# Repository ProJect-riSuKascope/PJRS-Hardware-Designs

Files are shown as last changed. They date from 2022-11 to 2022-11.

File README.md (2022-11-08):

# Project RisukaScope硬件系统
硬件系统主要分为以下几个部分：

## 电源
`/Power`文件夹。  
一个基于XL4016/SY8253的6~9V/5V/3.3V三轨供电系统。
此外还有一个给模拟前端用的5V模拟电源输出，用了一个LM1117-5.0。  
这部分十分臃肿，所以之后会做一个新的出来。

## 射频前端
`/RFFE`文件夹。  
前端LNA+滤波+多级Gain Block放大。  
前端LNA是NXP的BGU8009 GNSS LNA。  
滤波器是TA2494A。SAW滤波器，中心频率1420MHz，带宽80MHz。  
Gain Block用的是烂大街的SBB5089。  
Qucs仿真得到这个电路的增益~56dB，NF~0.66dB；实测增益48dB，NF因条件有限未测试。

## 调谐器与ADC
`Tuner ADC`文件夹。调谐器用的是各类SDR设备上常见的MSI001芯片，只用了L Band端口。实际试了一下应该有8MHz的带宽。  
ADC用的是AD9201，I/Q双通道同步采样ADC。  
系统采样率16MSPS。

## 通信与用户界面
`/Connectivity Interface`文件夹。
用了个ESP32-C3实现蓝牙/Wi-Fi通信。ESP32-C3通过SPI连接到FPGA。  
CD4504做缓冲器驱动舵机。  
预留了RGB LCD和以太网模块的接口。但目前还没用上。  
下面预留了八个机械键盘轴和两个电位器的位置，用于机械结构的操控。  
但后来想了想，感觉这样一点也不好用，不如直接遥控了。  
因为很多东西都没啥卵用，所以这部分也要大改。

## PMOD-Flash TinyRTC
`PMOD-Flash`文件夹。  
仿照Arduino平台上曾红极一时的I2C TinyRTC模块设计的PMOD Flash+RTC模块。  
一个W25N01 Flash+RX8010 RTC。RTC备份电源用的是硬币状的超级电容器。

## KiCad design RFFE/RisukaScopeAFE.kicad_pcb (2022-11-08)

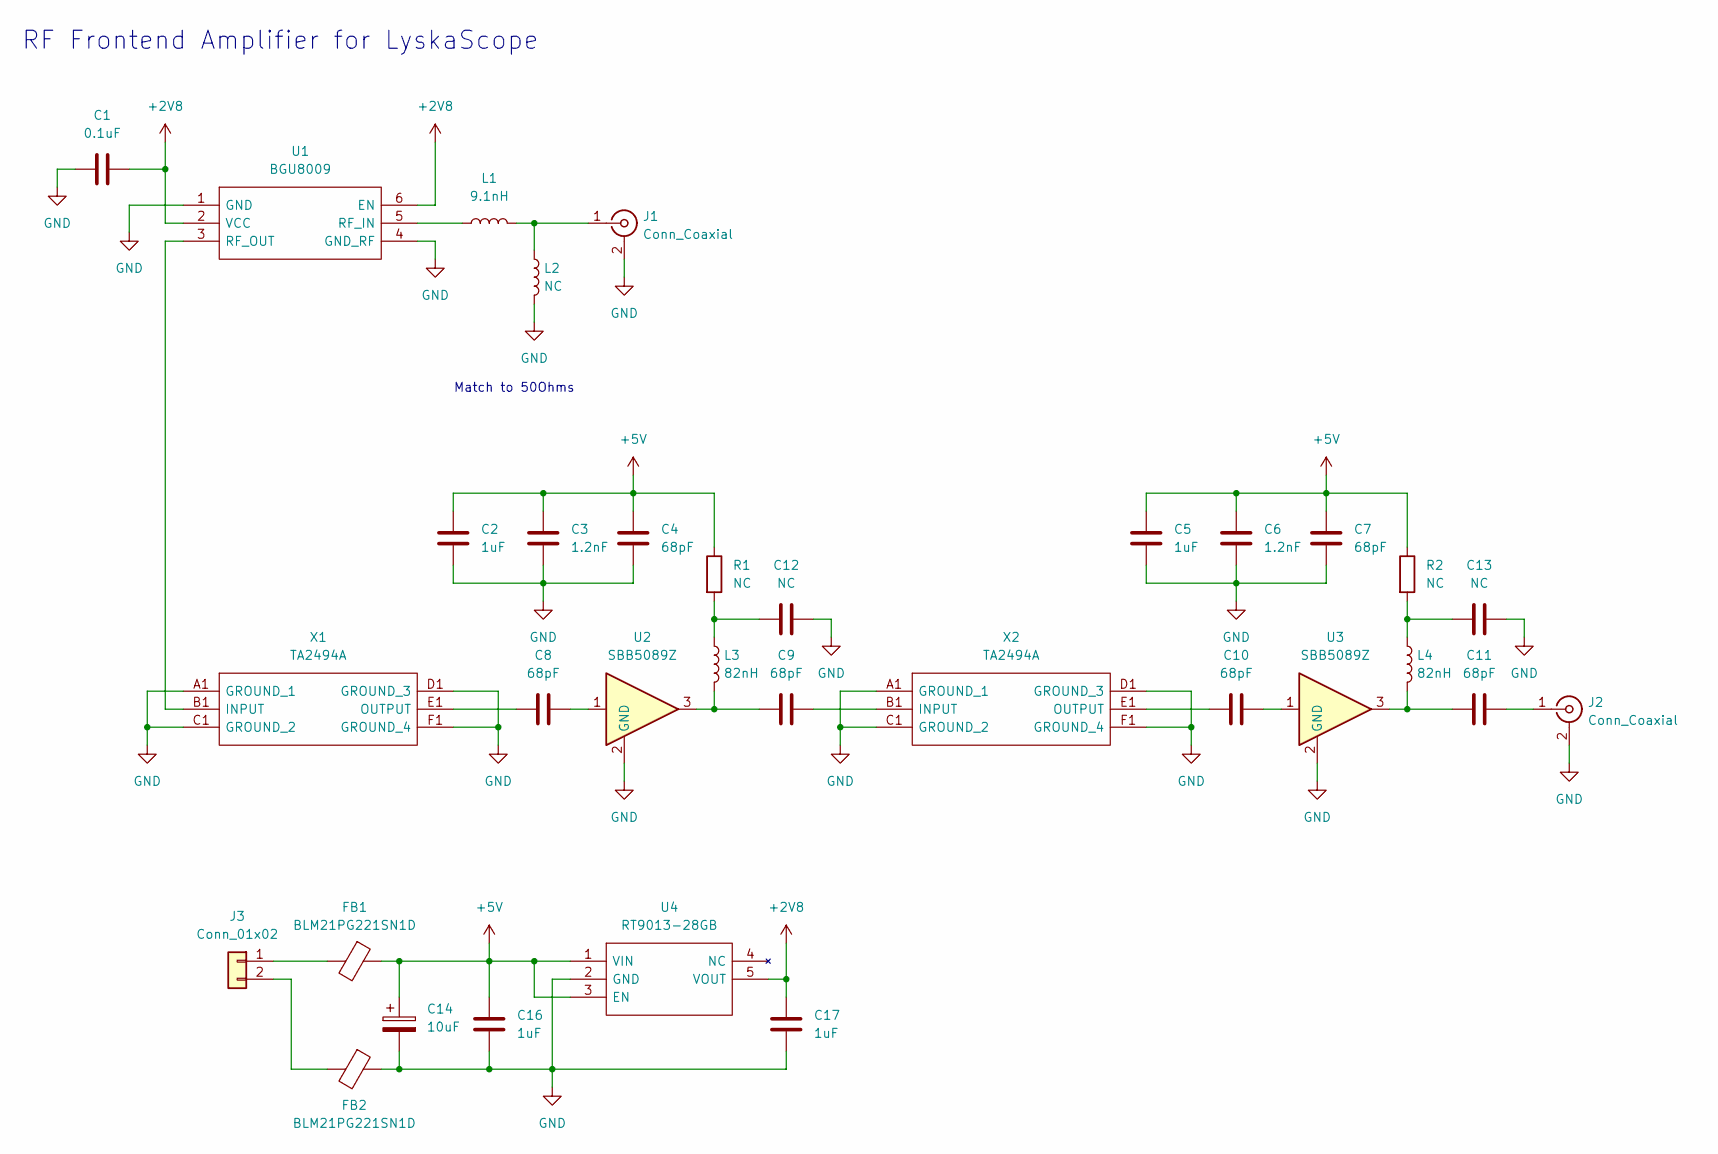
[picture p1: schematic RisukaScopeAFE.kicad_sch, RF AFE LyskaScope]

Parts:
C1: 0.1uF; C_0603_1608Metric
C2, C5, C16, C17: 1uF; C_0603_1608Metric
C3, C6: 1.2nF; C_0603_1608Metric
C4, C7, C8, C9, C10, C11: 68pF; C_0603_1608Metric
C12, C13: NC; C_0603_1608Metric
C14: 10uF; CP_EIA-3216-18_Kemet-A
FB1, FB2: BLM21PG221SN1D; L_0805_2012Metric
J1, J2: Conn_Coaxial; SMA_Samtec_SMA-J-P-X-ST-EM1_EdgeMount
J3: Conn_01x02; PinHeader_1x02_P2.54mm_Vertical
L1: 9.1nH; L_0603_1608Metric
L2: NC; L_0603_1608Metric
L3, L4: 82nH; L_0603_1608Metric
R1, R2: NC; R_0805_2012Metric
U1: BGU8009; SL3S1013FTB0115; Manufacturer_Part_Number BGU7005,115; Mouser Part Number 771-BGU7005115
U2, U3: SBB5089Z; SOT-89-3
U4: RT9013-28GB; SOT94P279X130-5N; Manufacturer_Part_Number RT9013-33GB
X1, X2: TA2494A; Manufacturer_Part_Number TA2494A

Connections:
+2V8: C1.1, C17.1, U1.2 (VCC), U1.6 (EN), U4.5 (VOUT)
+5V: C2.1, C3.1, C4.1, C5.1, C6.1, C7.1, C14.1, C16.1, FB1.1, R1.1, R2.1, U4.1 (VIN), U4.3 (EN)
GND: C1.2, C2.2, C3.2, C4.2, C5.2, C6.2, C7.2, C12.2, C13.2, C14.2, C16.2, C17.2, FB2.1, J1.2 (Ext), J2.2 (Ext), L2.2, U1.1 (GND), U1.4 (GND_RF), U2.2 (GND), U3.2 (GND), U4.2 (GND), X1.A1 (GROUND_1), X1.C1 (GROUND_2), X1.D1 (GROUND_3), X1.F1 (GROUND_4), X2.A1 (GROUND_1), X2.C1 (GROUND_2), X2.D1 (GROUND_3), X2.F1 (GROUND_4)
unnamed: C8.1, U2.1
unnamed: C8.2, X1.E1 (OUTPUT)
unnamed: C9.1, X2.B1 (INPUT)
unnamed: C9.2, L3.2, U2.3
unnamed: C10.1, U3.1
unnamed: C10.2, X2.E1 (OUTPUT)
unnamed: C11.1, J2.1 (In)
unnamed: C11.2, L4.2, U3.3
unnamed: FB1.2, J3.1
unnamed: FB2.2, J3.2
unnamed: J1.1 (In), L1.2, L2.1
unnamed: L1.1, U1.5 (RF_IN)
unnamed: C12.1, L3.1, R1.2
unnamed: C13.1, L4.1, R2.2
unnamed: U1.3 (RF_OUT), X1.B1 (INPUT)

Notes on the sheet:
Match to 50Ohms
RF Frontend Amplifier for LyskaScope

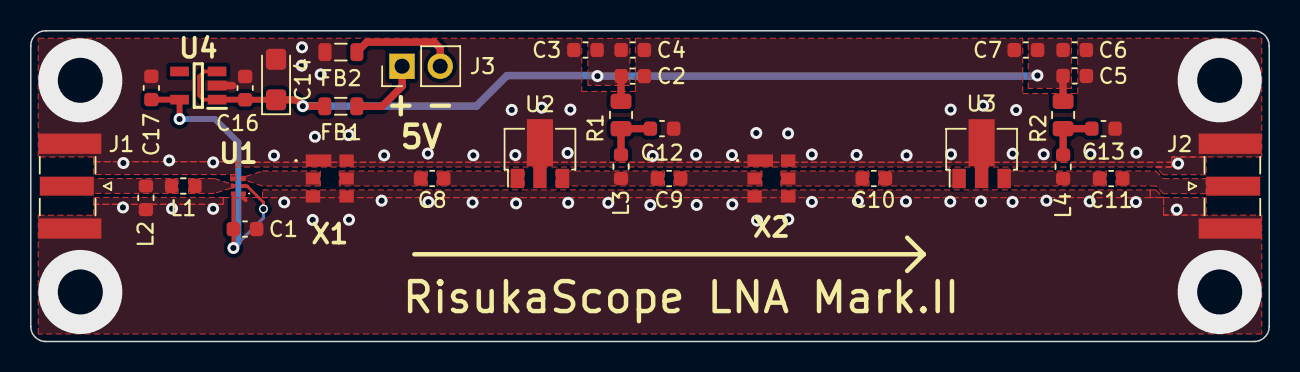
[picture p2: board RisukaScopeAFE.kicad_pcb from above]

Board: 2 copper layers, 82.5 x 20.7 mm, 33 parts (0 on the bottom side), 18 nets.

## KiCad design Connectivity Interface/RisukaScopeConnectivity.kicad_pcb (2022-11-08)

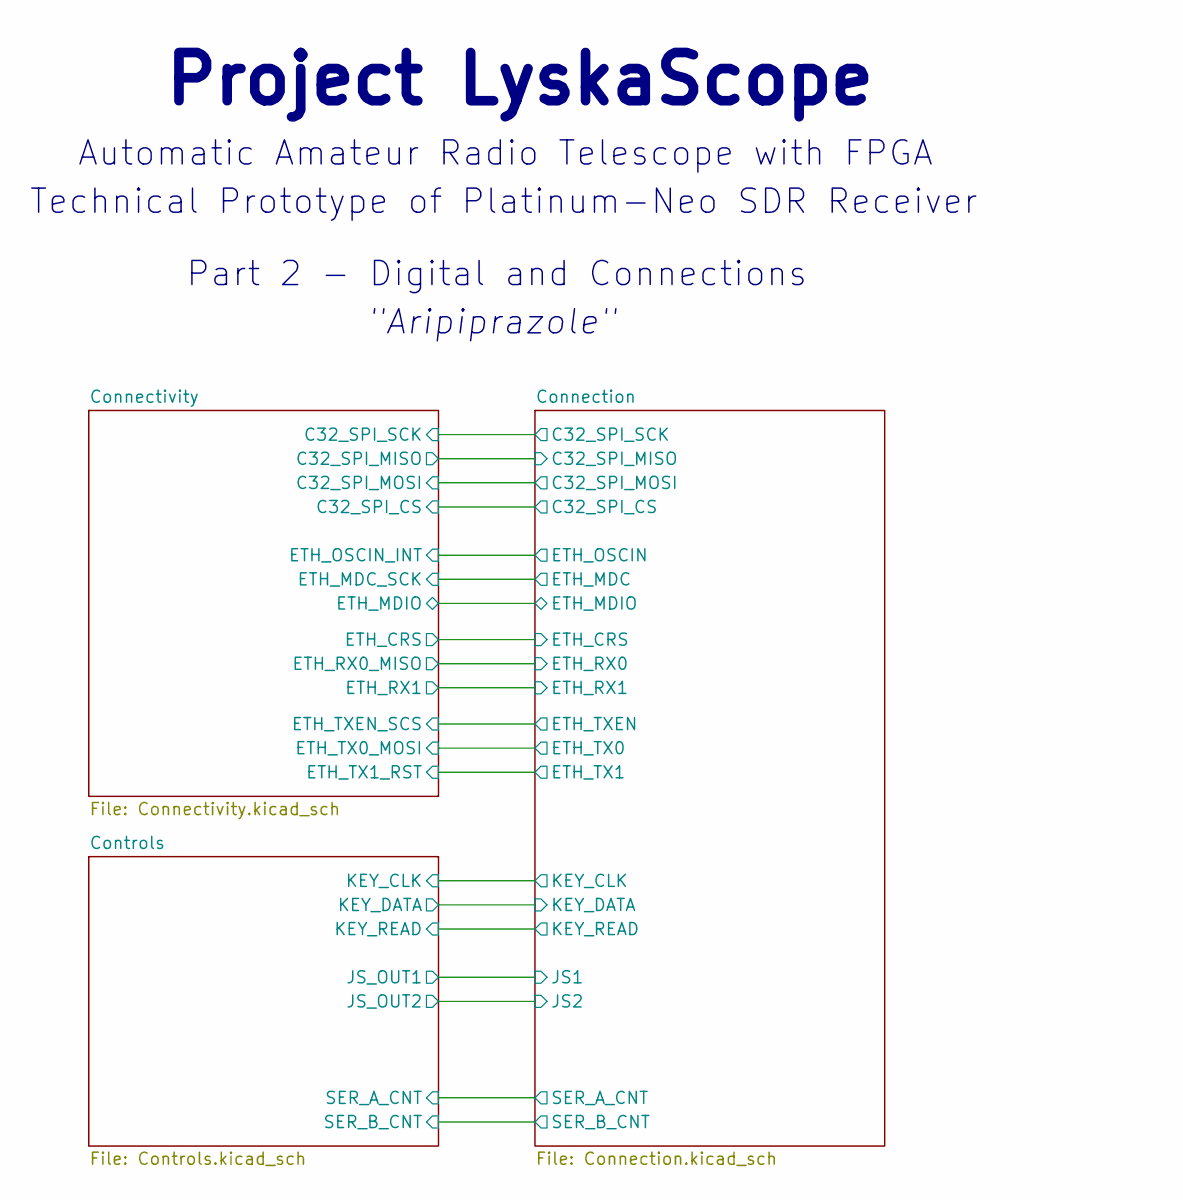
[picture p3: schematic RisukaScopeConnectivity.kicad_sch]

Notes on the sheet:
Project LyskaScope
Technical Prototype of Platinum-Neo SDR Receiver
"Aripiprazole"
Part 2 - Digital and Connections
Automatic Amateur Radio Telescope with FPGA

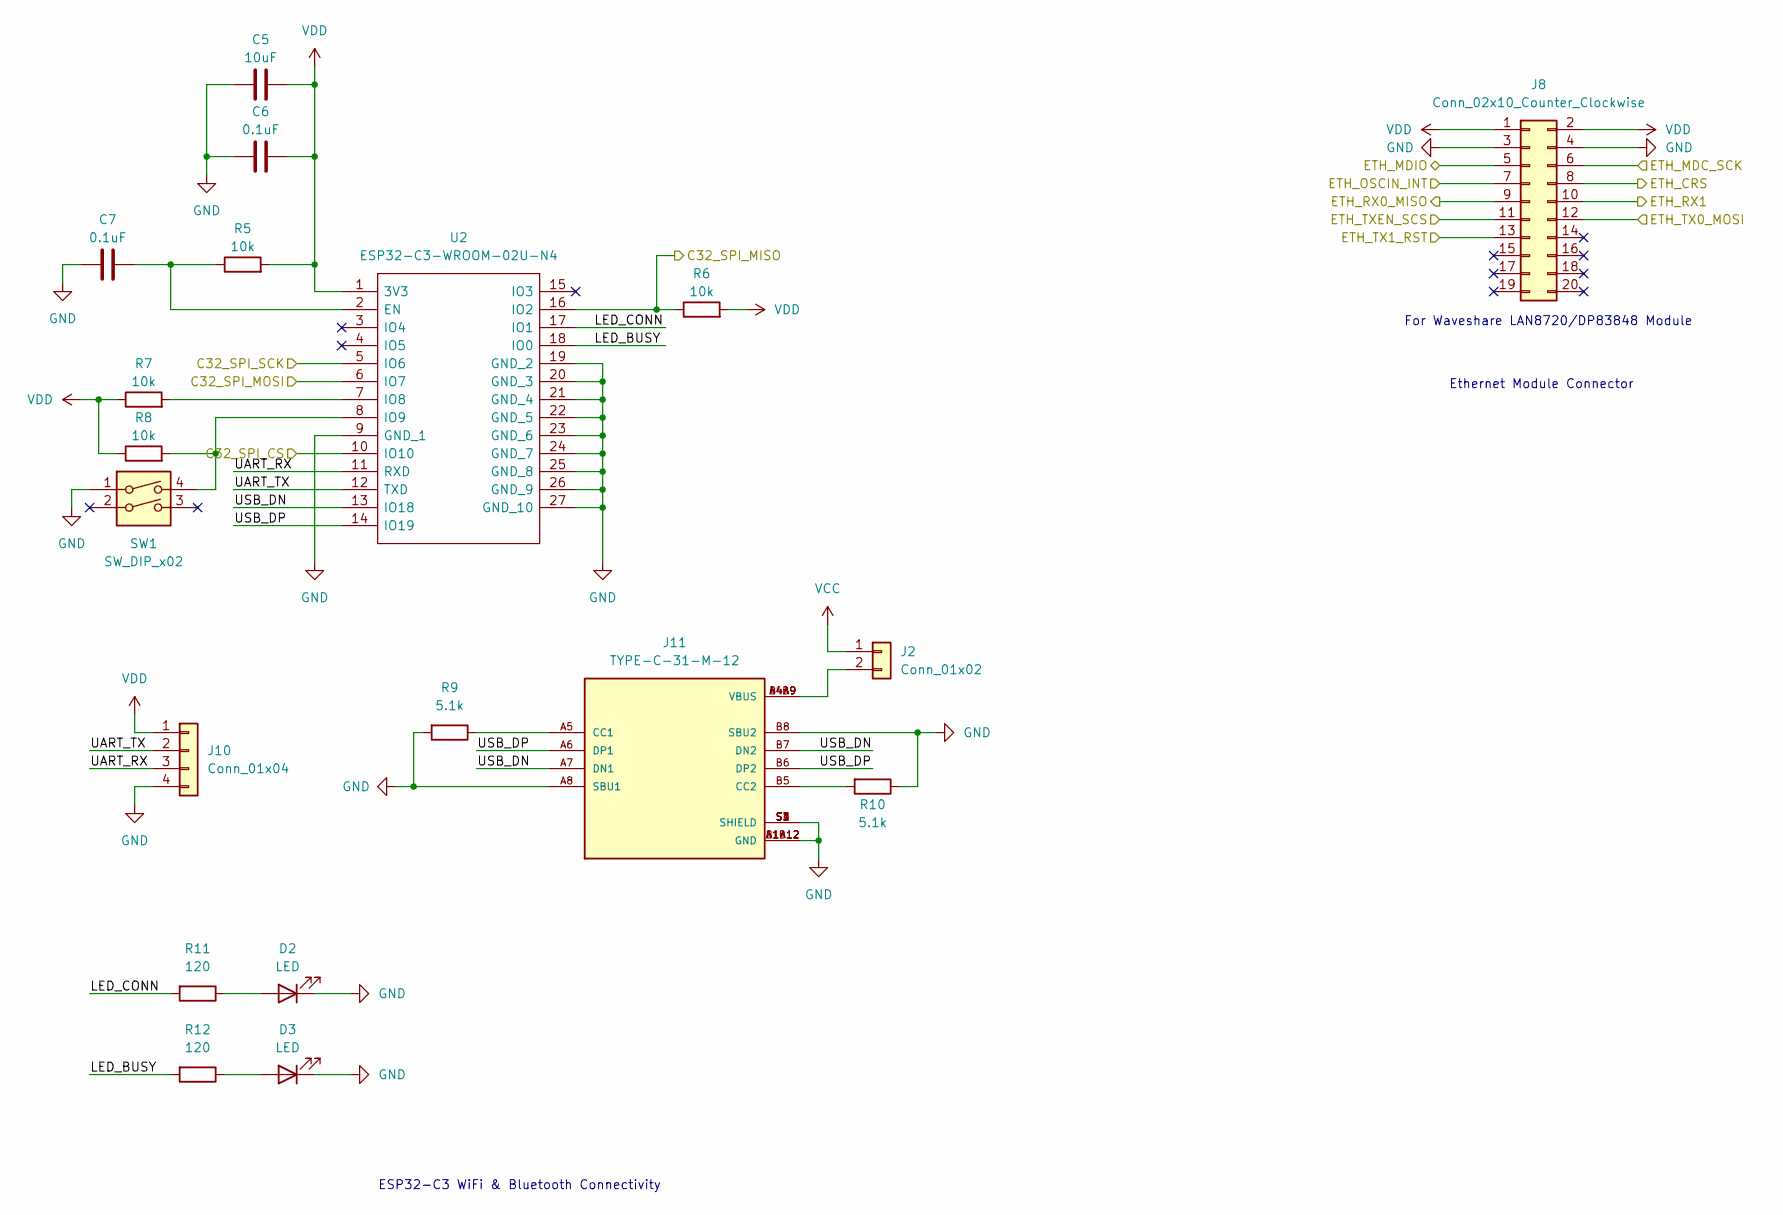
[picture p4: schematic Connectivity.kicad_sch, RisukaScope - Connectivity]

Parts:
C5: 10uF; C_0603_1608Metric
C6, C7: 0.1uF; C_0603_1608Metric
D2, D3: LED; LED_0603_1608Metric
J2: Conn_01x02; PinHeader_1x02_P2.54mm_Vertical
J8: Conn_02x10_Counter_Clockwise; PinHeader_2x10_P2.54mm_Vertical
J10: Conn_01x04; PinHeader_1x04_P2.54mm_Vertical
J11: TYPE-C-31-M-12; HRO_TYPE-C-31-M-12; PARTREV A
R5, R6, R7, R8: 10k; R_0603_1608Metric
R9, R10: 5.1k; R_0603_1608Metric
R11, R12: 120; R_0603_1608Metric
SW1: SW_DIP_x02; DSHP02TSGET
U2: ESP32-C3-WROOM-02U-N4; ESP32C3WROOM02UN4; Manufacturer_Part_Number ESP32-C3-WROOM-02U-N4; Mouser Part Number 356-ESP32C3WROM02UN4

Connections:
/Connection/C32_SPI_CS: U2.10 (IO10); also elsewhere on the board
/Connection/C32_SPI_MISO: R6.1, U2.16 (IO2); also elsewhere on the board
/Connection/C32_SPI_MOSI: U2.6 (IO7); also elsewhere on the board
/Connection/C32_SPI_SCK: U2.5 (IO6); also elsewhere on the board
/Connection/ETH_CRS: J8.8; also elsewhere on the board
/Connection/ETH_MDC: J8.6; also elsewhere on the board
/Connection/ETH_MDIO: J8.5; also elsewhere on the board
/Connection/ETH_OSCIN: J8.7; also elsewhere on the board
/Connection/ETH_RX0: J8.9; also elsewhere on the board
/Connection/ETH_RX1: J8.10; also elsewhere on the board
/Connection/ETH_TX0: J8.12; also elsewhere on the board
/Connection/ETH_TX1: J8.13; also elsewhere on the board
/Connection/ETH_TXEN: J8.11; also elsewhere on the board
/Connectivity/LED_BUSY: R12.2, U2.18 (IO0)
/Connectivity/LED_CONN: R11.2, U2.17 (IO1)
/Connectivity/UART_RX: J10.3, U2.11 (RXD)
/Connectivity/UART_TX: J10.2, U2.12 (TXD)
/Connectivity/USB_DN: J11.A7 (DN1), J11.B7 (DN2), U2.13 (IO18)
/Connectivity/USB_DP: J11.A6 (DP1), J11.B6 (DP2), U2.14 (IO19)
GND: C5.2, C6.2, C7.2, D2.1 (K), D3.1 (K), J8.3, J8.4, J10.4, J11.A1B12 (GND), J11.A8 (SBU1), J11.B1A12 (GND), J11.B8 (SBU2), J11.S1 (SHIELD), J11.S2 (SHIELD), J11.S3 (SHIELD), J11.S4 (SHIELD), R9.2, R10.1, SW1.1, U2.9 (GND_1), U2.19 (GND_2), U2.20 (GND_3), U2.21 (GND_4), U2.22 (GND_5), U2.23 (GND_6), U2.24 (GND_7), U2.25 (GND_8), U2.26 (GND_9), U2.27 (GND_10); also elsewhere on the board
unnamed: C7.1, R5.1, U2.2 (EN)
unnamed: D2.2 (A), R11.1
unnamed: D3.2 (A), R12.1
unnamed: J2.2, J11.A4B9 (VBUS), J11.B4A9 (VBUS)
unnamed: J11.A5 (CC1), R9.1
unnamed: J11.B5 (CC2), R10.2
unnamed: R7.2, U2.7 (IO8)
unnamed: R8.2, SW1.4, U2.8 (IO9)
VCC: J2.1; also elsewhere on the board
VDD: C5.1, C6.1, J8.1, J8.2, J10.1, R5.2, R6.2, R7.1, R8.1, U2.1 (3V3); also elsewhere on the board

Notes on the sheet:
Ethernet Module Connector
ESP32-C3 WiFi & Bluetooth Connectivity
For Waveshare LAN8720/DP83848 Module

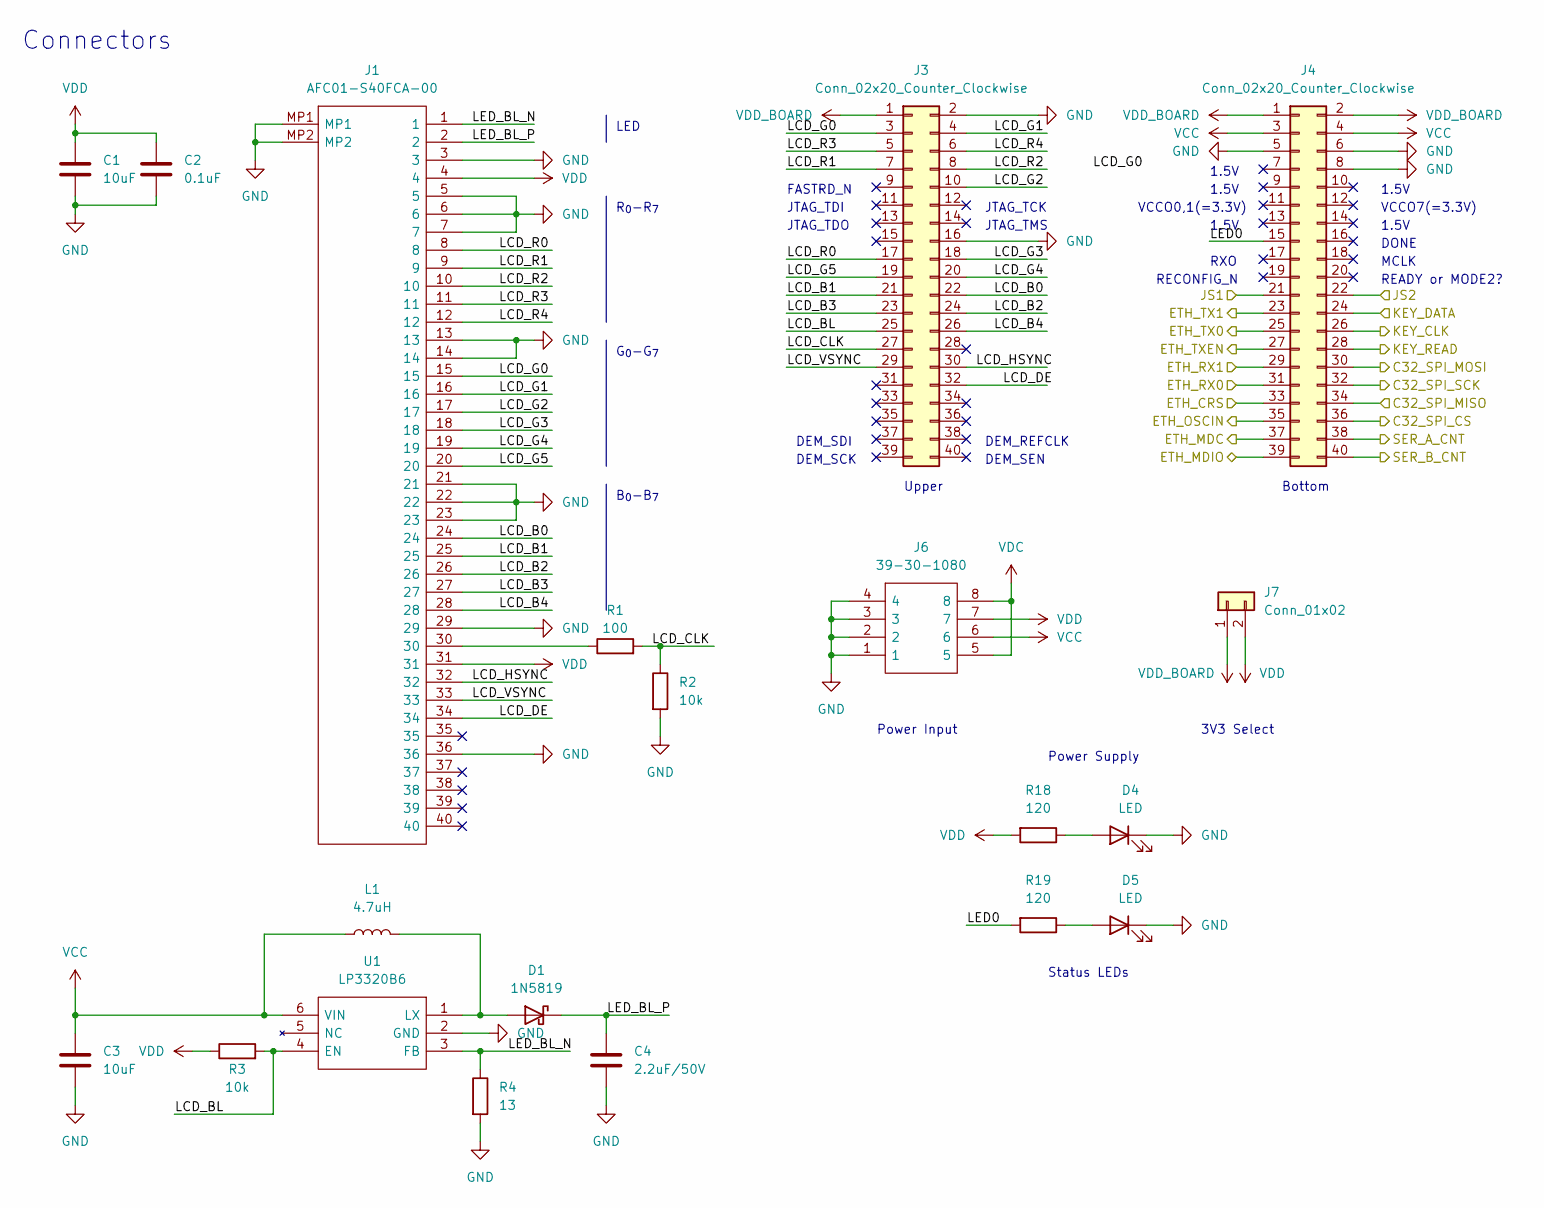
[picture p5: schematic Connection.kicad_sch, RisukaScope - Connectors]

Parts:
C1, C3: 10uF; C_0603_1608Metric
C2: 0.1uF; C_0603_1608Metric
C4: 2.2uF/50V; C_0805_2012Metric
D1: 1N5819; D_SOD-323
D4, D5: LED; LED_0603_1608Metric
J1: AFC01-S40FCA-00; AFC01S40FCA00; Manufacturer_Part_Number AFC01-S40FCA-00
J3, J4: Conn_02x20_Counter_Clockwise; PinHeader_2x20_P2.54mm_Vertical
J6: 39-30-1080; 39-30-Y080; Manufacturer_Part_Number 39-30-1080; Mouser Part Number 538-39-30-1080
J7: Conn_01x02; PinHeader_1x02_P2.54mm_Vertical
L1: 4.7uH; INDPM3030X150N
R1: 100; R_0603_1608Metric
R2, R3: 10k; R_0603_1608Metric
R4: 13; R_0603_1608Metric
R18, R19: 120; R_0603_1608Metric
U1: LP3320B6; SOT94P279X130-6N; Manufacturer_Part_Number LP3320B6

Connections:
/Connection/C32_SPI_CS: J4.36; also elsewhere on the board
/Connection/C32_SPI_MISO: J4.34; also elsewhere on the board
/Connection/C32_SPI_MOSI: J4.30; also elsewhere on the board
/Connection/C32_SPI_SCK: J4.32; also elsewhere on the board
/Connection/ETH_CRS: J4.33; also elsewhere on the board
/Connection/ETH_MDC: J4.37; also elsewhere on the board
/Connection/ETH_MDIO: J4.39; also elsewhere on the board
/Connection/ETH_OSCIN: J4.35; also elsewhere on the board
/Connection/ETH_RX0: J4.31; also elsewhere on the board
/Connection/ETH_RX1: J4.29; also elsewhere on the board
/Connection/ETH_TX0: J4.25; also elsewhere on the board
/Connection/ETH_TX1: J4.23; also elsewhere on the board
/Connection/ETH_TXEN: J4.27; also elsewhere on the board
/Connection/JS1: J4.21; also elsewhere on the board
/Connection/JS2: J4.22; also elsewhere on the board
/Connection/KEY_CLK: J4.26; also elsewhere on the board
/Connection/KEY_DATA: J4.24; also elsewhere on the board
/Connection/KEY_READ: J4.28; also elsewhere on the board
/Connection/LCD_B0: J1.24, J3.22
/Connection/LCD_B1: J1.25, J3.21
/Connection/LCD_B2: J1.26, J3.24
/Connection/LCD_B3: J1.27, J3.23
/Connection/LCD_B4: J1.28, J3.26
/Connection/LCD_BL: J3.25, R3.2, U1.4 (EN)
/Connection/LCD_CLK: J3.27, R1.2, R2.1
/Connection/LCD_DE: J1.34, J3.32
/Connection/LCD_G0: J1.15, J3.3
/Connection/LCD_G1: J1.16, J3.4
/Connection/LCD_G2: J1.17, J3.10
/Connection/LCD_G3: J1.18, J3.18
/Connection/LCD_G4: J1.19, J3.20
/Connection/LCD_G5: J1.20, J3.19
/Connection/LCD_HSYNC: J1.32, J3.30
/Connection/LCD_R0: J1.8, J3.17
/Connection/LCD_R1: J1.9, J3.7
/Connection/LCD_R2: J1.10, J3.8
/Connection/LCD_R3: J1.11, J3.5
/Connection/LCD_R4: J1.12, J3.6
/Connection/LCD_VSYNC: J1.33, J3.29
/Connection/LED0: J4.15, R19.2
/Connection/LED_BL_N: J1.1, R4.1, U1.3 (FB)
/Connection/LED_BL_P: C4.1, D1.1 (K), J1.2
/Connection/SER_A_CNT: J4.38; also elsewhere on the board
/Connection/SER_B_CNT: J4.40; also elsewhere on the board
GND: C1.2, C2.2, C3.2, C4.2, D4.1 (K), D5.1 (K), J1.3, J1.5, J1.6, J1.7, J1.13, J1.14, J1.21, J1.22, J1.23, J1.29, J1.36, J1.MP1, J1.MP2, J3.2, J3.16, J4.5, J4.6, J4.8, J6.1, J6.2, J6.3, J6.4, R2.2, R4.2, U1.2 (GND); also elsewhere on the board
unnamed: D1.2 (A), L1.2, U1.1 (LX)
unnamed: D4.2 (A), R18.1
unnamed: D5.2 (A), R19.1
unnamed: J1.30, R1.1
VCC: C3.1, J4.3, J4.4, J6.6, L1.1, U1.6 (VIN); also elsewhere on the board
VDC: J6.5, J6.8; also elsewhere on the board
VDD: C1.1, C2.1, J1.4, J1.31, J6.7, J7.2, R3.1, R18.2; also elsewhere on the board
VDD_BOARD: J3.1, J4.1, J4.2, J7.1

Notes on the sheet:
1.5V
RECONFIG_N
R_{0}-R_{7}
Upper
DEM_SDI
DEM_SEN
JTAG_TDI
3V3 Select
MCLK
RXO
DONE
VCCO7(=3.3V)
JTAG_TCK
JTAG_TMS
JTAG_TDO
LED
Connectors
Bottom
DEM_REFCLK
DEM_SCK
READY or MODE2?
FASTRD_N
Power Input
G_{0}-G_{7}
VCCO0,1(=3.3V)
Status LEDs
B_{0}-B_{7}
Power Supply

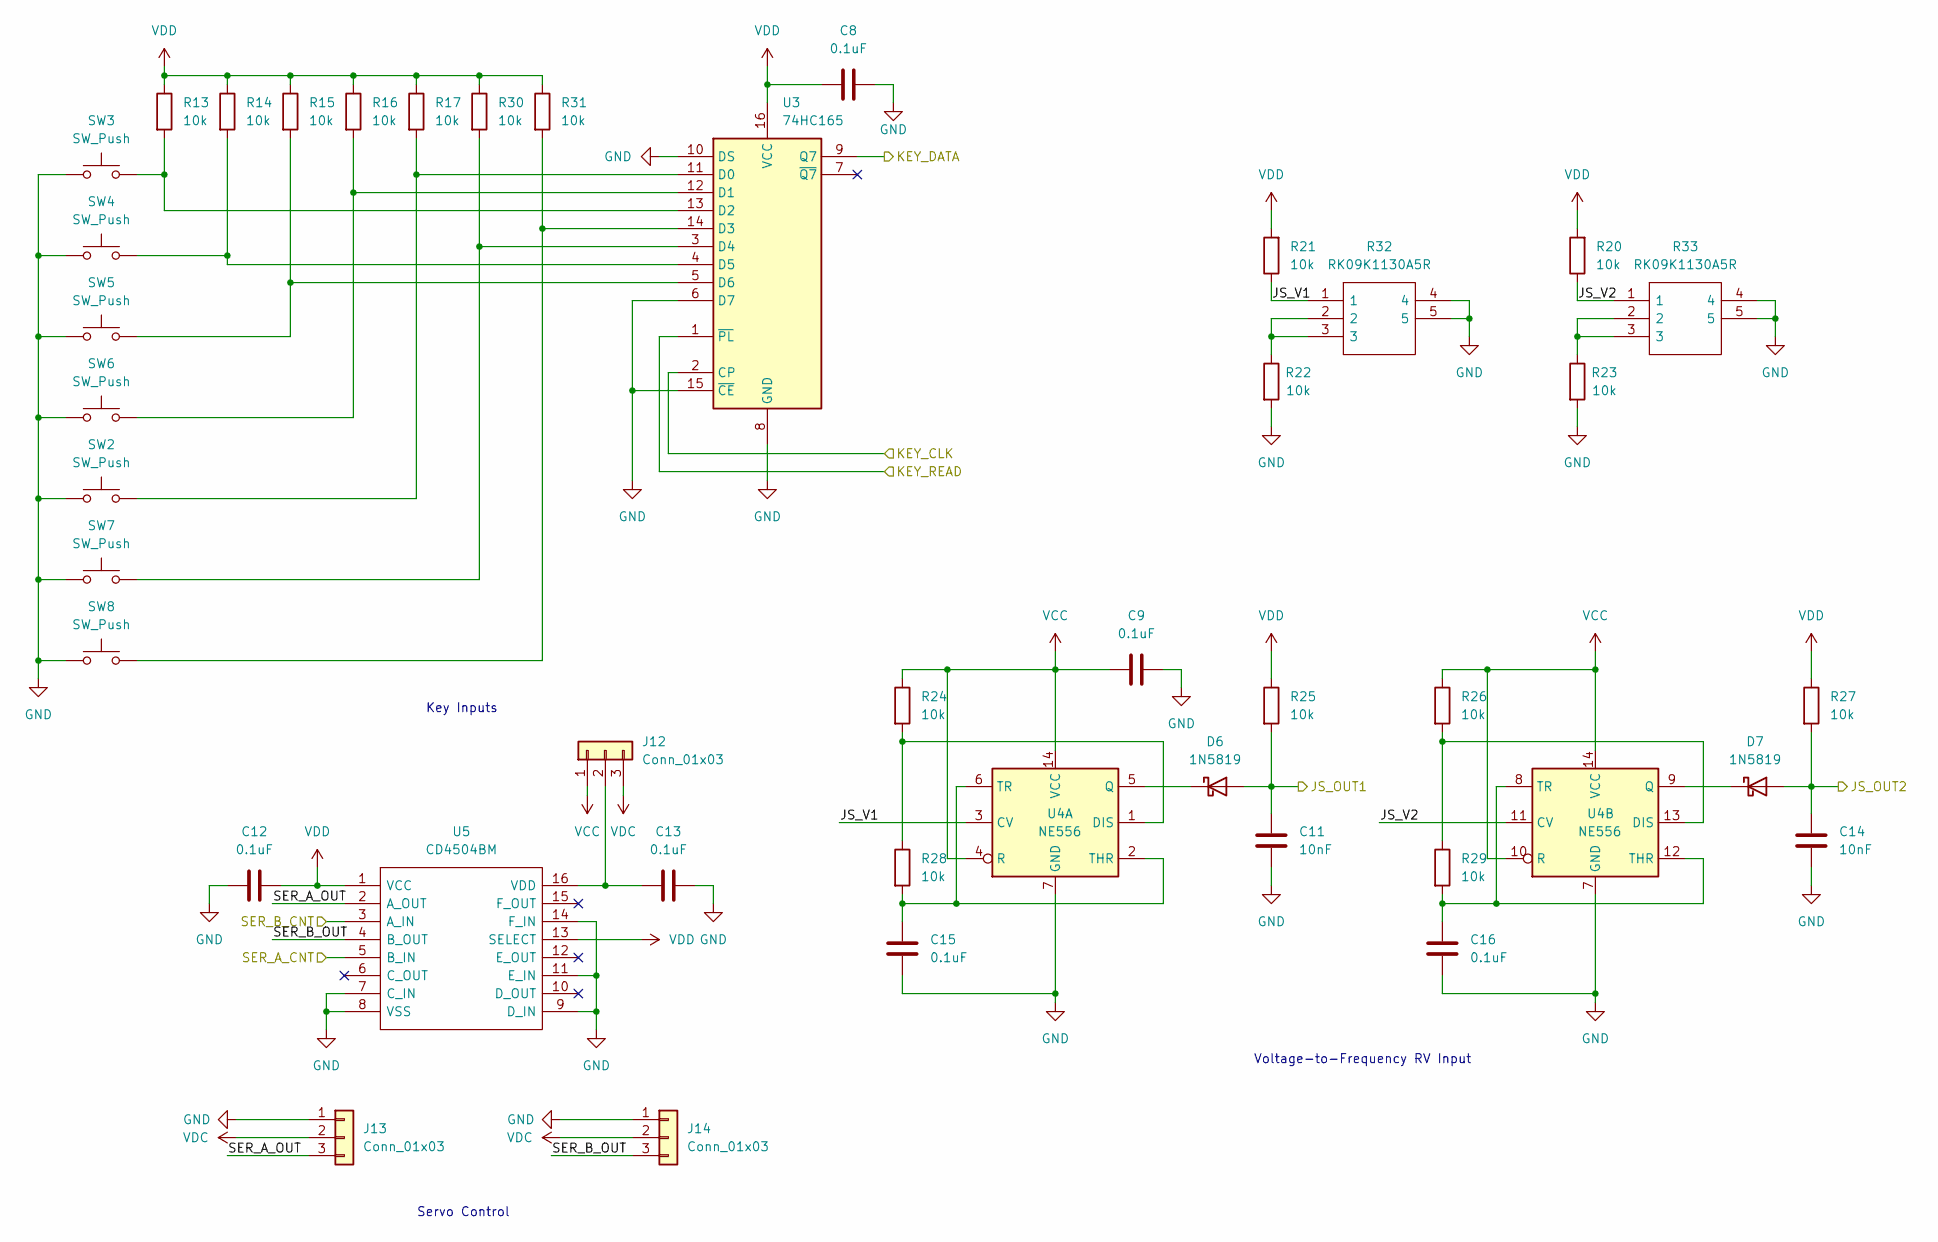
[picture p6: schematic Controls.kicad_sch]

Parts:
C8, C9, C12, C13, C15, C16: 0.1uF; C_0603_1608Metric
C11, C14: 10nF; C_0603_1608Metric
D6, D7: 1N5819; D_SOD-323
J12, J13, J14: Conn_01x03; PinHeader_1x03_P2.54mm_Vertical
R13, R14, R15, R16, R17, R20, R21, R22, R23, R24, R25, R26, R27, R28, R29, R30, R31: 10k; R_0603_1608Metric
R32, R33: RK09K1130A5R; Manufacturer_Part_Number RK09K1130A5R; Mouser Part Number 688-RK09K1130A5R
SW2, SW3, SW4, SW5, SW6: SW_Push; CPG135001D03
SW7, SW8: SW_Push; CPG135001D03_1U5
U3: 74HC165; SOP-16_3.9x9.9mm_P1.27mm
U4: NE556; SOIC-14_3.9x8.7mm_P1.27mm
U5: CD4504BM; SOIC127P600X175-16N; Manufacturer_Part_Number CD4504BM; Mouser Part Number 595-CD4504BM

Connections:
/Connection/JS1: C11.1, D6.2 (A), R25.2; also elsewhere on the board
/Connection/JS2: C14.1, D7.2 (A), R27.2; also elsewhere on the board
/Connection/KEY_CLK: U3.2 (CP); also elsewhere on the board
/Connection/KEY_DATA: U3.9 (Q7); also elsewhere on the board
/Connection/KEY_READ: U3.1 (~PL); also elsewhere on the board
/Connection/SER_A_CNT: U5.5 (B_IN); also elsewhere on the board
/Connection/SER_B_CNT: U5.3 (A_IN); also elsewhere on the board
/Controls/JS_V1: R21.1, R32.1, U4.3 (CV)
/Controls/JS_V2: R20.1, R33.1, U4.11 (CV)
/Controls/SER_A_OUT: J13.3, U5.2 (A_OUT)
/Controls/SER_B_OUT: J14.3, U5.4 (B_OUT)
GND: C8.2, C9.2, C11.2, C12.2, C13.1, C14.2, C15.2, C16.2, J13.1, J14.1, R22.2, R23.2, R32.4, R32.5, R33.4, R33.5, SW2.1, SW3.1, SW4.1, SW5.1, SW6.1, SW7.1, SW8.1, U3.6 (D7), U3.8 (GND), U3.10 (DS), U3.15 (~CE), U4.7 (GND), U5.7 (C_IN), U5.8 (VSS), U5.9 (D_IN), U5.11 (E_IN), U5.14 (F_IN); also elsewhere on the board
unnamed: C13.2, J12.2, U5.16 (VDD)
unnamed: C15.1, R28.2, U4.2 (THR), U4.6 (TR)
unnamed: C16.1, R29.2, U4.8 (TR), U4.12 (THR)
unnamed: D6.1 (K), U4.5 (Q)
unnamed: D7.1 (K), U4.9 (Q)
unnamed: R13.2, SW3.2, U3.13 (D2)
unnamed: R14.2, SW4.2, U3.4 (D5)
unnamed: R15.2, SW5.2, U3.5 (D6)
unnamed: R16.2, SW6.2, U3.12 (D1)
unnamed: R17.2, SW2.2, U3.11 (D0)
unnamed: R22.1, R32.2, R32.3
unnamed: R23.1, R33.2, R33.3
unnamed: R24.2, R28.1, U4.1 (DIS)
unnamed: R26.2, R29.1, U4.13 (DIS)
unnamed: R30.2, SW7.2, U3.3 (D4)
unnamed: R31.2, SW8.2, U3.14 (D3)
VCC: C9.1, J12.1, R24.1, R26.1, U4.4 (R), U4.10 (R), U4.14 (VCC); also elsewhere on the board
VDC: J12.3, J13.2, J14.2; also elsewhere on the board
VDD: C8.1, C12.1, R13.1, R14.1, R15.1, R16.1, R17.1, R20.2, R21.2, R25.1, R27.1, R30.1, R31.1, U3.16 (VCC), U5.1 (VCC), U5.13 (SELECT); also elsewhere on the board

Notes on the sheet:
Servo Control
Key Inputs
Voltage-to-Frequency RV Input

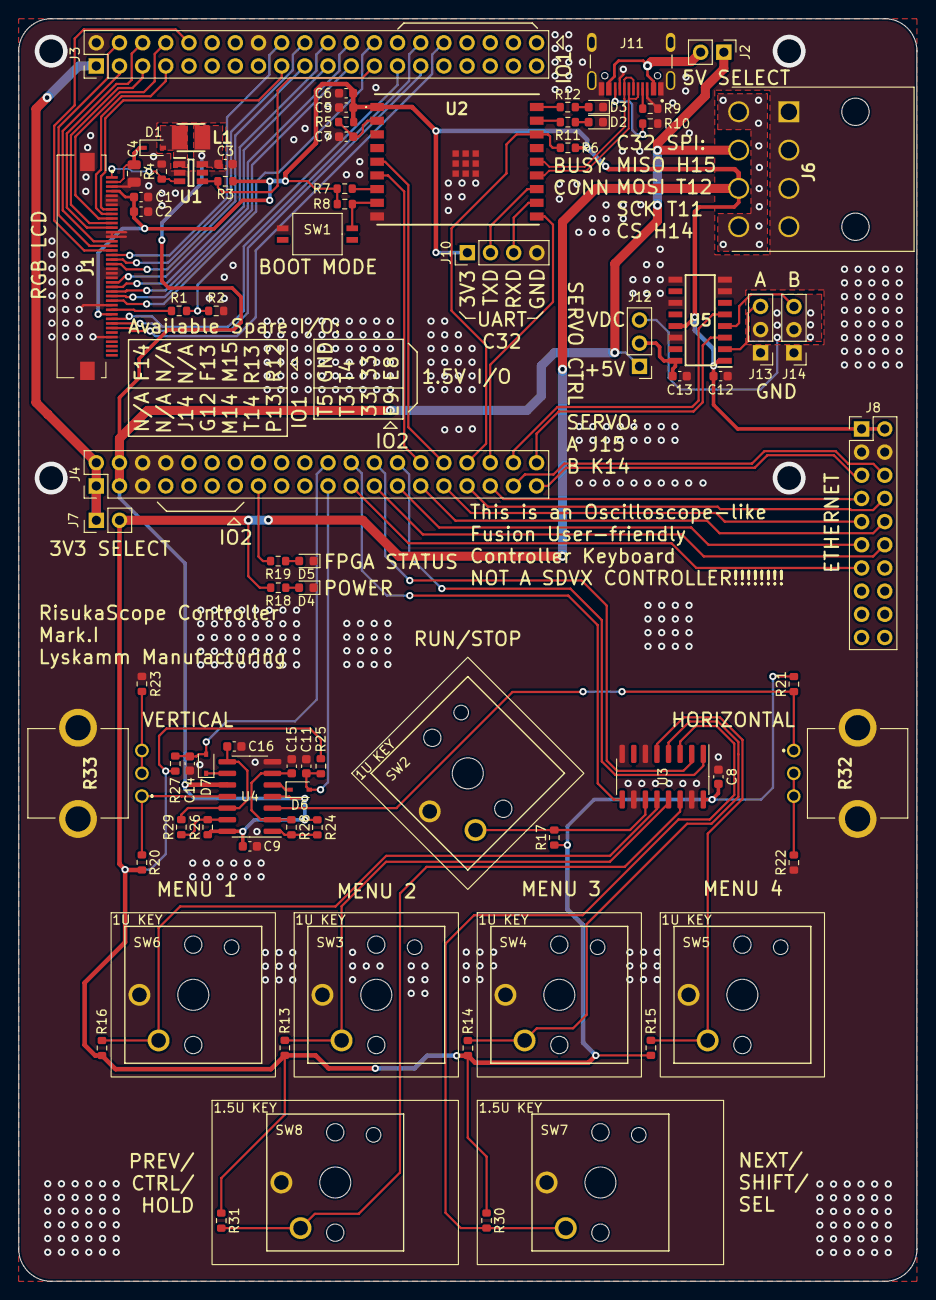
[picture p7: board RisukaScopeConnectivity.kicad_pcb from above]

Board: 2 copper layers, 98.5 x 138.4 mm, 81 parts (0 on the bottom side), 87 nets.

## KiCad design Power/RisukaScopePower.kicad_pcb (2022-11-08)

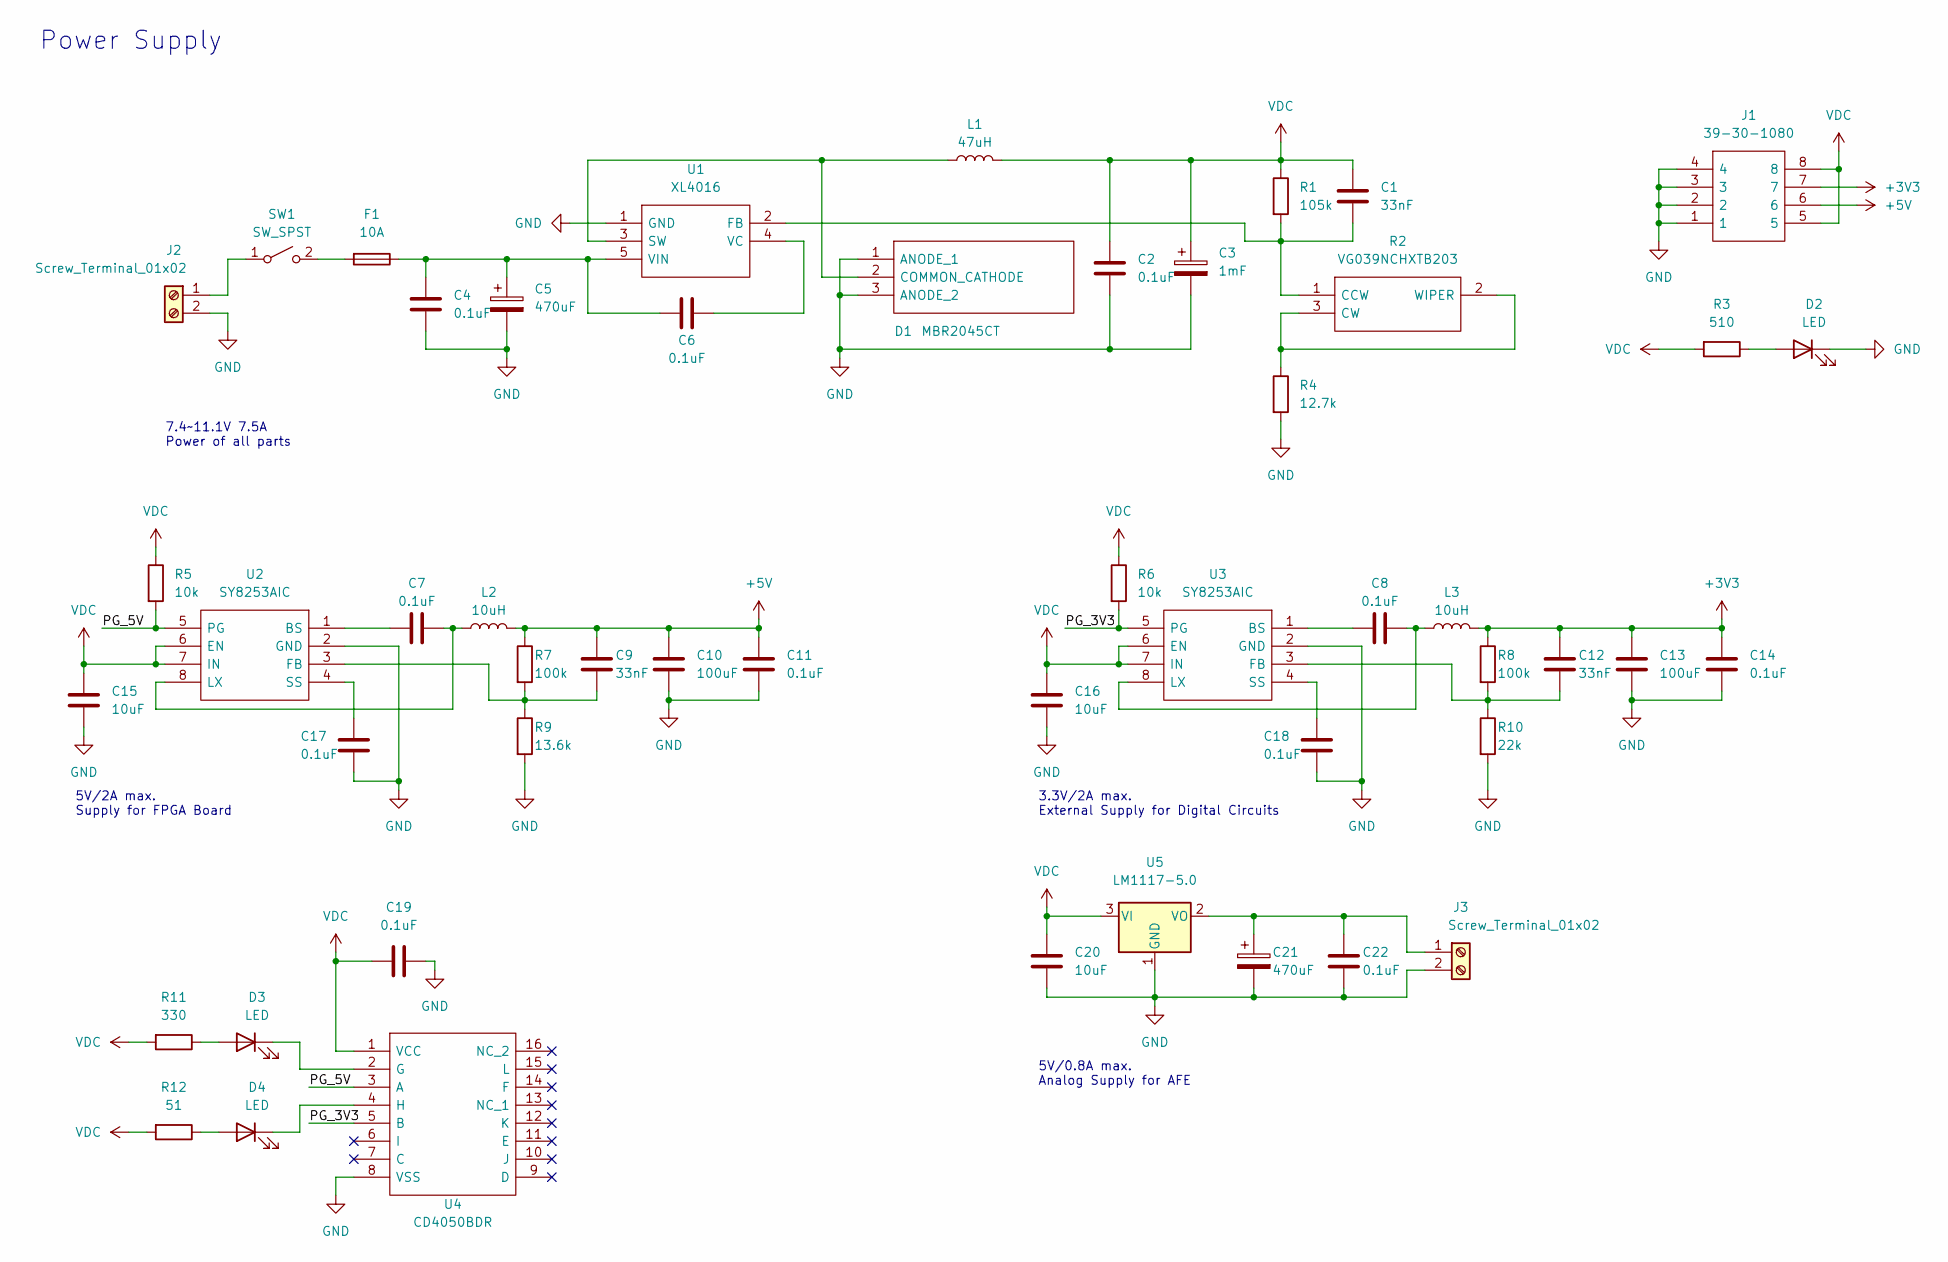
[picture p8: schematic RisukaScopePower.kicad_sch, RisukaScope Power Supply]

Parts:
C1, C9, C12: 33nF; C_0603_1608Metric
C2, C4, C6, C7, C8, C11, C14, C17, C18, C19, C22: 0.1uF; C_0603_1608Metric
C3: 1mF; CP_Radial_D10.0mm_P5.00mm
C5, C21: 470uF; CP_Elec_10x10.5
C10, C13: 100uF; C_1206_3216Metric
C15, C16, C20: 10uF; C_0603_1608Metric
D1: MBR2045CT; TO254P450X1000X2010-3P; Manufacturer_Part_Number MBR2045CT; Mouser Part Number 621-MBR2045CT
D2, D3, D4: LED; LED_0603_1608Metric
F1: 10A; 64600001003
J1: 39-30-1080; 39-30-Y080; Manufacturer_Part_Number 39-30-1080; Mouser Part Number 538-39-30-1080
J2, J3: Screw_Terminal_01x02; TerminalBlock_MetzConnect_Type101_RT01602HBWC_1x02_P5.08mm_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
L1: 47uH; L_Toroid_Vertical_L21.6mm_W9.5mm_P7.11mm_Pulse_C
L2, L3: 10uH; INDPM5452X300N
R1: 105k; R_0603_1608Metric
R2: VG039NCHXTB203; Manufacturer_Part_Number VG039NCHXTB203
R3: 510; R_0805_2012Metric
R4: 12.7k; R_0603_1608Metric
R5, R6: 10k; R_0603_1608Metric
R7, R8: 100k; R_0603_1608Metric
R9: 13.6k; R_0603_1608Metric
R10: 22k; R_0603_1608Metric
R11: 330; R_0805_2012Metric
R12: 51; R_0805_2012Metric
SW1: SW_SPST; SS11-BBIWQ-R20-R
U1: XL4016; Manufacturer_Part_Number XL4016
U2, U3: SY8253AIC; SOT65P280X110-8N; Manufacturer_Part_Number SY8253AIC
U4: CD4050BDR; SOIC127P600X175-16N; Manufacturer_Part_Number CD4050BDR; Mouser Part Number 595-CD4050BDR
U5: LM1117-5.0; TO-220-3_Vertical

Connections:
+3V3: C12.1, C13.1, C14.1, J1.7, L3.2, R8.1
+5V: C9.1, C10.1, C11.1, J1.6, L2.2, R7.1
/PG_3V3: R6.2, U3.5 (PG), U4.5 (B)
/PG_5V: R5.2, U2.5 (PG), U4.3 (A)
GND: C2.2, C3.2, C4.2, C5.2, C10.2, C11.2, C13.2, C14.2, C15.2, C16.2, C17.2, C18.2, C19.2, C20.2, C21.2, C22.2, D1.1 (ANODE_1), D1.3 (ANODE_2), D2.1 (K), J1.1, J1.2, J1.3, J1.4, J2.2, J3.2, R4.2, R9.2, R10.2, U1.1 (GND), U2.2 (GND), U3.2 (GND), U4.8 (VSS), U5.1 (GND)
unnamed: C1.2, R1.2, R2.1 (CCW), U1.2 (FB)
unnamed: C4.1, C5.1, C6.2, F1.1, U1.5 (VIN)
unnamed: C6.1, U1.4 (VC)
unnamed: C7.1, U2.1 (BS)
unnamed: C7.2, L2.1, U2.8 (LX)
unnamed: C8.1, U3.1 (BS)
unnamed: C8.2, L3.1, U3.8 (LX)
unnamed: C9.2, R7.2, R9.1, U2.3 (FB)
unnamed: C12.2, R8.2, R10.1, U3.3 (FB)
unnamed: C17.1, U2.4 (SS)
unnamed: C18.1, U3.4 (SS)
unnamed: C21.1, C22.1, J3.1, U5.2 (VO)
unnamed: D1.2 (COMMON_CATHODE), L1.1, U1.3 (SW)
unnamed: D2.2 (A), R3.1
unnamed: D3.1 (K), U4.2 (G)
unnamed: D3.2 (A), R11.1
unnamed: D4.1 (K), U4.4 (H)
unnamed: D4.2 (A), R12.1
unnamed: F1.2, SW1.2 (B)
unnamed: J2.1, SW1.1 (A)
unnamed: R2.2 (WIPER), R2.3 (CW), R4.1
VDC: C1.1, C2.1, C3.1, C15.1, C16.1, C19.1, C20.1, J1.5, J1.8, L1.2, R1.1, R3.2, R5.1, R6.1, R11.2, R12.2, U2.6 (EN), U2.7 (IN), U3.6 (EN), U3.7 (IN), U4.1 (VCC), U5.3 (VI)

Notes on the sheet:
7.4~11.1V 7.5A Power of all parts
Power Supply
5V/0.8A max. Analog Supply for AFE
5V/2A max. Supply for FPGA Board
3.3V/2A max. External Supply for Digital Circuits

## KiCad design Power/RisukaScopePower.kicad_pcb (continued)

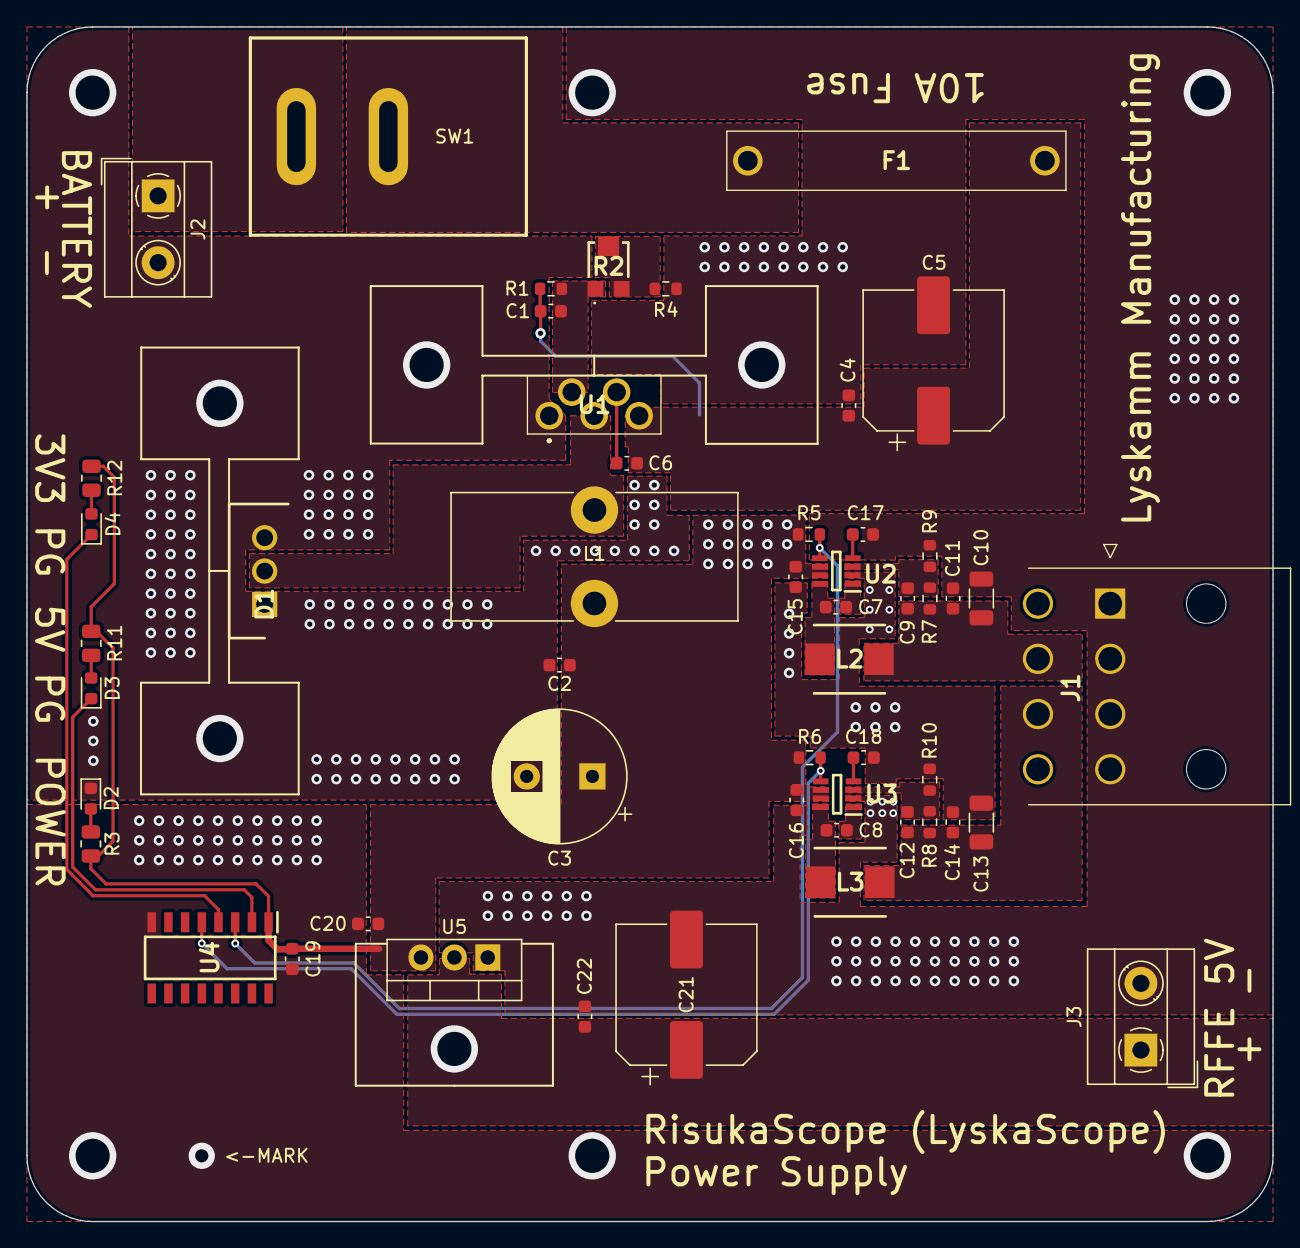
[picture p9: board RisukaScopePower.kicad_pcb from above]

Board: 2 copper layers, 94.8 x 90.9 mm, 51 parts (0 on the bottom side), 27 nets.

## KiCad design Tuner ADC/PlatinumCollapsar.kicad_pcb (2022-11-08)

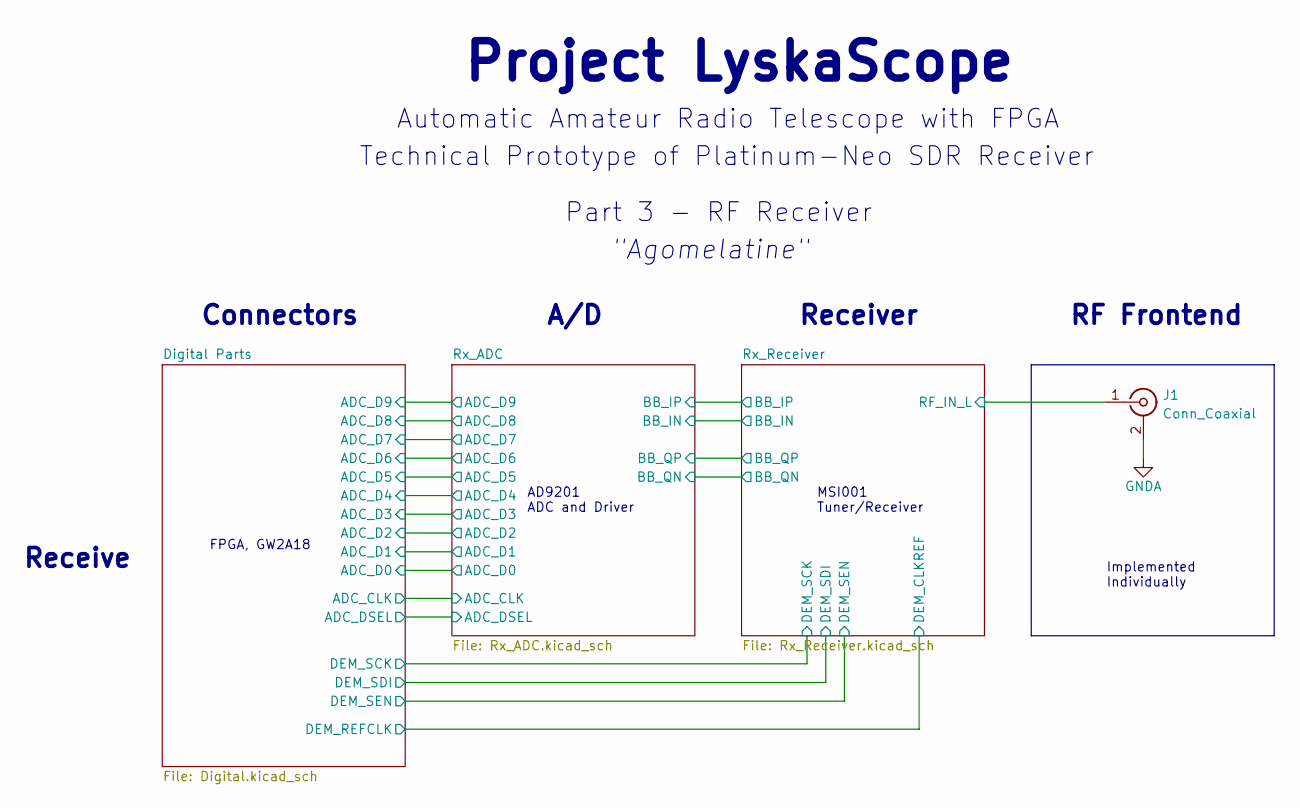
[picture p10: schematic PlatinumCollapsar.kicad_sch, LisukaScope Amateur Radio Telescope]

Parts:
J1: Conn_Coaxial; SMA_Samtec_SMA-J-P-X-ST-EM1_EdgeMount

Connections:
/Rx_Receiver/RF_IN_L: J1.1 (In); also elsewhere on the board

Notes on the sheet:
Connectors
Receive
FPGA, GW2A18
Technical Prototype of Platinum-Neo SDR Receiver
AD9201 ADC and Driver
Project LyskaScope
Receiver
Automatic Amateur Radio Telescope with FPGA
MSI001 Tuner/Receiver
Implemented Individually
RF Frontend
A/D
"Agomelatine"
Part 3 - RF Receiver

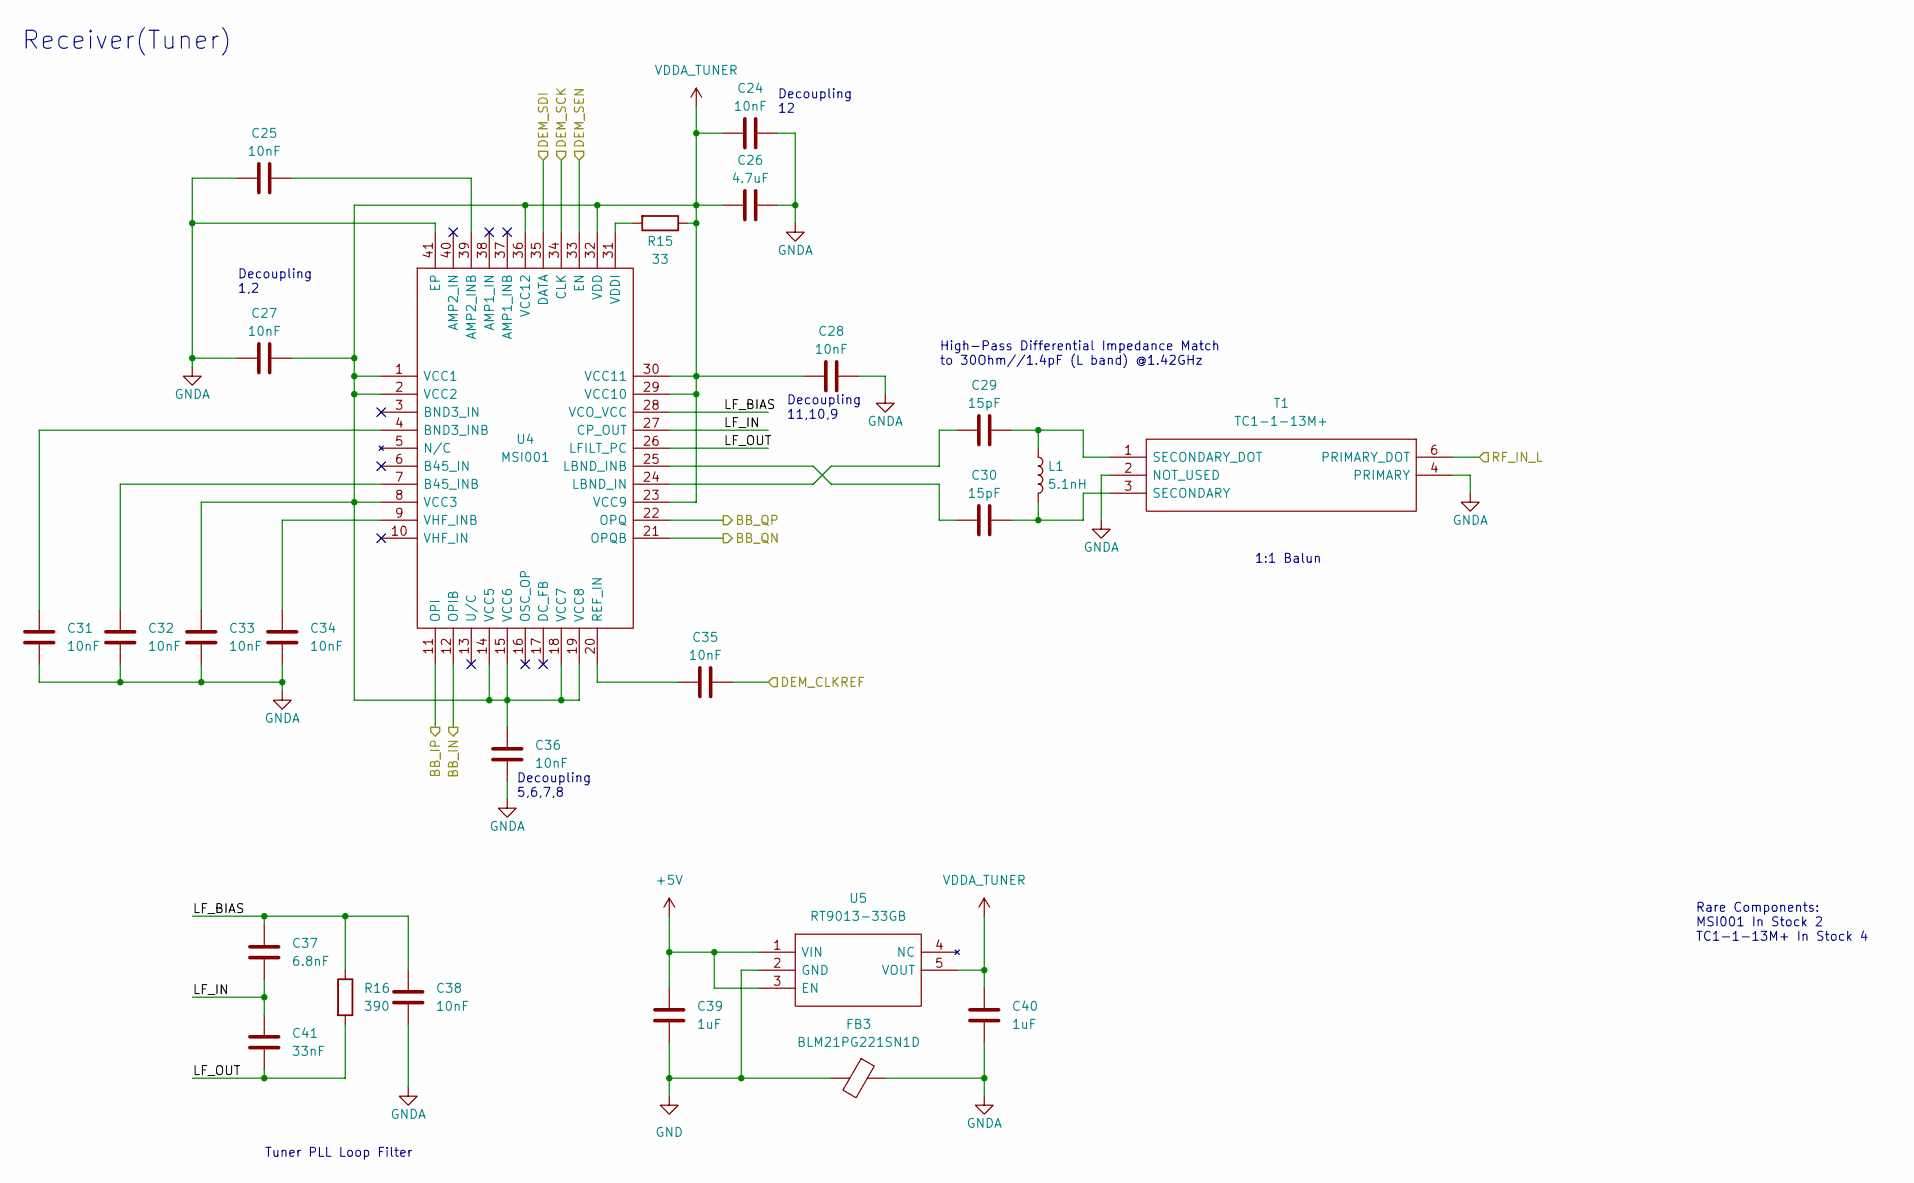
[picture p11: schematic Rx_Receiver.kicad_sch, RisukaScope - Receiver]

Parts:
C24, C25, C27, C28, C31, C32, C33, C34, C35, C36, C38: 10nF; C_0603_1608Metric
C26: 4.7uF; C_0603_1608Metric
C29, C30: 15pF; C_0603_1608Metric
C37: 6.8nF; C_0603_1608Metric
C39, C40: 1uF; C_0603_1608Metric
C41: 33nF; C_0603_1608Metric
FB3: BLM21PG221SN1D; L_0805_2012Metric
L1: 5.1nH; L_0603_1608Metric
R15: 33; R_0603_1608Metric
R16: 390; R_0603_1608Metric
T1: TC1-1-13M+; TC414; Manufacturer_Part_Number TC1-1-13M+; Mouser Part Number 139-TC1-1-13M
U4: MSI001; QFN50P600X600X90-41N-D; Manufacturer_Part_Number MSI001
U5: RT9013-33GB; SOT94P279X130-5N; Manufacturer_Part_Number RT9013-33GB

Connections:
+5V: C39.1, U5.1 (VIN), U5.3 (EN); also elsewhere on the board
/Digital Parts/DEM_REFCLK: C35.2; also elsewhere on the board
/Digital Parts/DEM_SCK: U4.34 (CLK); also elsewhere on the board
/Digital Parts/DEM_SDI: U4.35 (DATA); also elsewhere on the board
/Digital Parts/DEM_SEN: U4.33 (EN); also elsewhere on the board
/Rx_ADC/BB_IN: U4.12 (OPIB); also elsewhere on the board
/Rx_ADC/BB_IP: U4.11 (OPI); also elsewhere on the board
/Rx_ADC/BB_QN: U4.21 (OPQB); also elsewhere on the board
/Rx_ADC/BB_QP: U4.22 (OPQ); also elsewhere on the board
/Rx_Receiver/LF_BIAS: C37.1, C38.1, R16.1, U4.28 (VCO_VCC)
/Rx_Receiver/LF_IN: C37.2, C41.1, U4.27 (CP_OUT)
/Rx_Receiver/LF_OUT: C41.2, R16.2, U4.26 (LFILT_PC)
/Rx_Receiver/RF_IN_L: T1.6 (PRIMARY_DOT); also elsewhere on the board
GND: C39.2, FB3.2, U5.2 (GND); also elsewhere on the board
unnamed: C25.2, U4.39 (AMP2_INB)
unnamed: C29.1, U4.24 (LBND_IN)
unnamed: C29.2, L1.1, T1.1 (SECONDARY_DOT)
unnamed: C30.1, U4.25 (LBND_INB)
unnamed: C30.2, L1.2, T1.3 (SECONDARY)
unnamed: C31.1, U4.4 (BND3_INB)
unnamed: C32.1, U4.7 (B45_INB)
unnamed: C34.1, U4.9 (VHF_INB)
unnamed: C35.1, U4.20 (REF_IN)
unnamed: R15.2, U4.31 (VDDI)
VDDA_TUNER: C24.1, C26.1, C27.2, C28.1, C33.1, C36.1, C40.1, R15.1, U4.1 (VCC1), U4.2 (VCC2), U4.8 (VCC3), U4.14 (VCC5), U4.15 (VCC6), U4.18 (VCC7), U4.19 (VCC8), U4.23 (VCC9), U4.29 (VCC10), U4.30 (VCC11), U4.32 (VDD), U4.36 (VCC12), U5.5 (VOUT)

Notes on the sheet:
Decoupling 12
Decoupling 11,10,9
1:1 Balun
Receiver(Tuner)
Decoupling 5,6,7,8
Tuner PLL Loop Filter
High-Pass Differential Impedance Match to 30Ohm//1.4pF (L band) @1.42GHz
Rare Components: MSI001 In Stock 2 TC1-1-13M+ In Stock 4
Decoupling 1,2

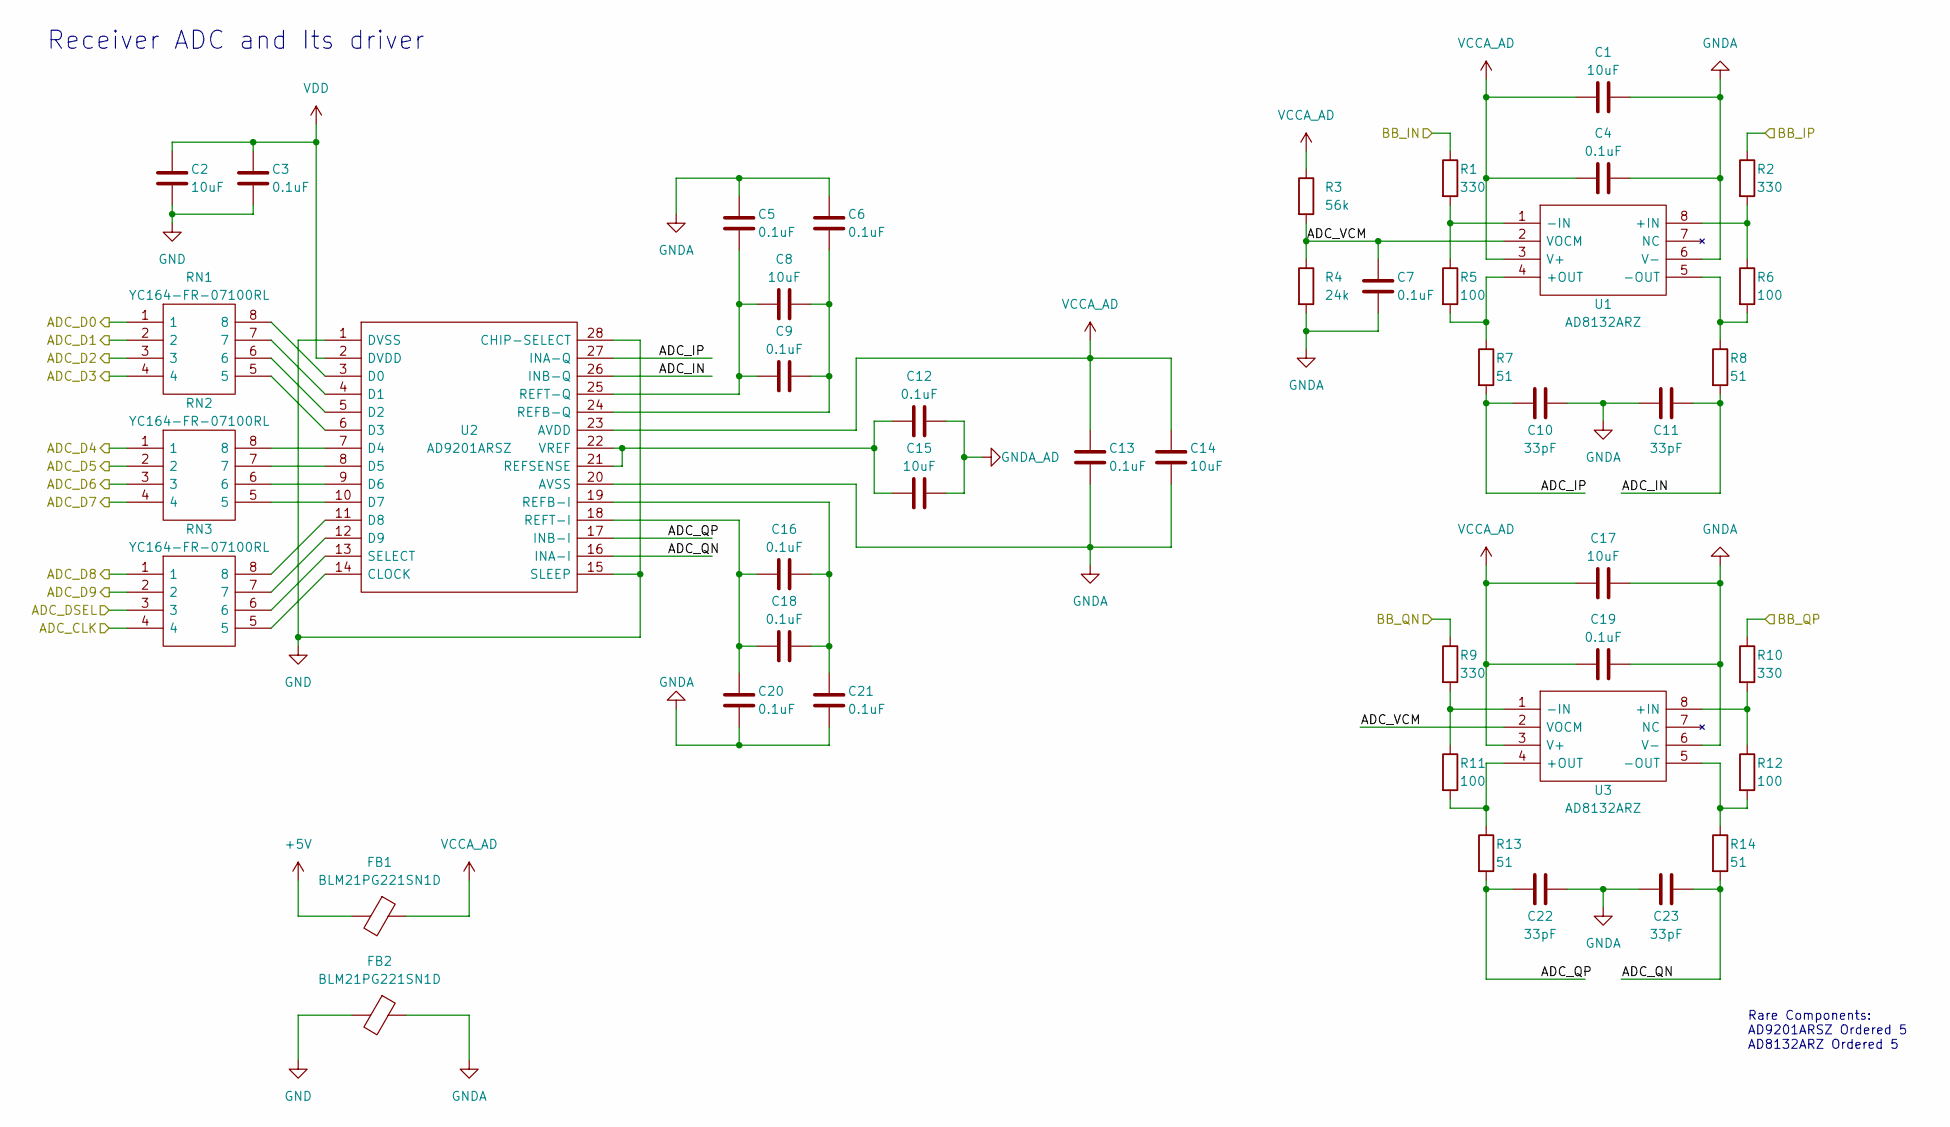
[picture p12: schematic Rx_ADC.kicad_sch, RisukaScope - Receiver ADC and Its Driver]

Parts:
C1, C2, C8, C14, C15, C17: 10uF; C_0603_1608Metric
C3, C4, C5, C6, C7, C9, C12, C13, C16, C18, C19, C20, C21: 0.1uF; C_0603_1608Metric
C10, C11, C22, C23: 33pF; C_0603_1608Metric
FB1, FB2: BLM21PG221SN1D; L_0805_2012Metric
R1, R2, R9, R10: 330; R_0603_1608Metric
R3: 56k; R_0603_1608Metric
R4: 24k; R_0603_1608Metric
R5, R6, R11, R12: 100; R_0603_1608Metric
R7, R8, R13, R14: 51; R_0603_1608Metric
RN1, RN2, RN3: YC164-FR-07100RL; YC164JR07220RL; Manufacturer_Part_Number YC164-FR-07100RL; Mouser Part Number 603-YC164-FR-07100RL
U1, U3: AD8132ARZ; SOIC127P600X175-8N; Manufacturer_Part_Number AD8132ARZ; Mouser Part Number 584-AD8132ARZ
U2: AD9201ARSZ; SOP65P777X198-28N; Manufacturer_Part_Number AD9201ARSZ; Mouser Part Number 584-AD9201ARSZ

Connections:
+5V: FB1.2; also elsewhere on the board
/Digital Parts/ADC_CLK: RN3.4; also elsewhere on the board
/Digital Parts/ADC_D0: RN1.1; also elsewhere on the board
/Digital Parts/ADC_D1: RN1.2; also elsewhere on the board
/Digital Parts/ADC_D2: RN1.3; also elsewhere on the board
/Digital Parts/ADC_D3: RN1.4; also elsewhere on the board
/Digital Parts/ADC_D4: RN2.1; also elsewhere on the board
/Digital Parts/ADC_D5: RN2.2; also elsewhere on the board
/Digital Parts/ADC_D6: RN2.3; also elsewhere on the board
/Digital Parts/ADC_D7: RN2.4; also elsewhere on the board
/Digital Parts/ADC_D8: RN3.1; also elsewhere on the board
/Digital Parts/ADC_D9: RN3.2; also elsewhere on the board
/Digital Parts/ADC_DSEL: RN3.3; also elsewhere on the board
/Rx_ADC/ADC_IN: C11.2, R8.2, U2.26 (INB-Q)
/Rx_ADC/ADC_IP: C10.1, R7.2, U2.27 (INA-Q)
/Rx_ADC/ADC_QN: C23.2, R14.2, U2.16 (INA-I)
/Rx_ADC/ADC_QP: C22.1, R13.2, U2.17 (INB-I)
/Rx_ADC/ADC_VCM: C7.1, R3.2, R4.1, U1.2 (VOCM), U3.2 (VOCM)
/Rx_ADC/BB_IN: R1.1; also elsewhere on the board
/Rx_ADC/BB_IP: R2.1; also elsewhere on the board
/Rx_ADC/BB_QN: R9.1; also elsewhere on the board
/Rx_ADC/BB_QP: R10.1; also elsewhere on the board
GND: C2.2, C3.2, FB2.2, U2.1 (DVSS), U2.15 (SLEEP), U2.28 (CHIP-SELECT); also elsewhere on the board
unnamed: C5.2, C8.1, C9.1, U2.25 (REFT-Q)
unnamed: C6.2, C8.2, C9.2, U2.24 (REFB-Q)
unnamed: C12.1, C15.1, U2.21 (REFSENSE), U2.22 (VREF)
unnamed: C16.1, C18.1, C20.1, U2.18 (REFT-I)
unnamed: C16.2, C18.2, C21.1, U2.19 (REFB-I)
unnamed: R1.2, R5.1, U1.1 (-IN)
unnamed: R2.2, R6.1, U1.8 (+IN)
unnamed: R5.2, R7.1, U1.4 (+OUT)
unnamed: R6.2, R8.1, U1.5 (-OUT)
unnamed: R10.2, R12.1, U3.8 (+IN)
unnamed: R9.2, R11.1, U3.1 (-IN)
unnamed: R11.2, R13.1, U3.4 (+OUT)
unnamed: R12.2, R14.1, U3.5 (-OUT)
unnamed: RN1.5, U2.6 (D3)
unnamed: RN1.6, U2.5 (D2)
unnamed: RN1.7, U2.4 (D1)
unnamed: RN1.8, U2.3 (D0)
unnamed: RN2.5, U2.10 (D7)
unnamed: RN2.6, U2.9 (D6)
unnamed: RN2.7, U2.8 (D5)
unnamed: RN2.8, U2.7 (D4)
unnamed: RN3.5, U2.14 (CLOCK)
unnamed: RN3.6, U2.13 (SELECT)
unnamed: RN3.7, U2.12 (D9)
unnamed: RN3.8, U2.11 (D8)
VCCA_AD: C1.1, C4.1, C13.1, C14.1, C17.1, C19.1, FB1.1, R3.1, U1.3 (V+), U2.23 (AVDD), U3.3 (V+)
VDD: C2.1, C3.1, U2.2 (DVDD); also elsewhere on the board

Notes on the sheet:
Rare Components: AD9201ARSZ Ordered 5 AD8132ARZ Ordered 5
Receiver ADC and Its driver


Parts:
J2, J5: Conn_02x06_Counter_Clockwise; PinHeader_2x06_P2.54mm_Vertical
J3, J4: Conn_02x20_Counter_Clockwise; PinHeader_2x20_P2.54mm_Vertical

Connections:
+5V: J4.3, J4.4; also elsewhere on the board
/Digital Parts/ADC_CLK: J5.12; also elsewhere on the board
/Digital Parts/ADC_D0: J2.6; also elsewhere on the board
/Digital Parts/ADC_D1: J2.8; also elsewhere on the board
/Digital Parts/ADC_D2: J2.10; also elsewhere on the board
/Digital Parts/ADC_D3: J2.12; also elsewhere on the board
/Digital Parts/ADC_D4: J2.11; also elsewhere on the board
/Digital Parts/ADC_D5: J2.9; also elsewhere on the board
/Digital Parts/ADC_D6: J5.7; also elsewhere on the board
/Digital Parts/ADC_D7: J5.5; also elsewhere on the board
/Digital Parts/ADC_D8: J5.6; also elsewhere on the board
/Digital Parts/ADC_D9: J5.8; also elsewhere on the board
/Digital Parts/ADC_DSEL: J5.10; also elsewhere on the board
/Digital Parts/DEM_REFCLK: J3.38; also elsewhere on the board
/Digital Parts/DEM_SCK: J3.39; also elsewhere on the board
/Digital Parts/DEM_SDI: J3.37; also elsewhere on the board
/Digital Parts/DEM_SEN: J3.40; also elsewhere on the board
GND: J2.3, J2.4, J3.2, J3.16, J4.5, J4.6, J4.8, J5.3, J5.4; also elsewhere on the board
VDD: J2.1, J2.2, J3.1; also elsewhere on the board

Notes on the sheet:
Upper
J7/Bottom Left
VDD
J6/Upper Left
Connectors
Bottom

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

Board: 2 copper layers, 88.0 x 53.9 mm, 75 parts (0 on the bottom side), 70 nets.

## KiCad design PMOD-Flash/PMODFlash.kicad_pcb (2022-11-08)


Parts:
C1, C3: 0.1uF; C_0603_1608Metric
C2: 1.5F; EECS5R5V155N
D1, D2: 1N5819HW; SOD3716X145N; Manufacturer_Part_Number 1N5819HW; Mouser Part Number N/A
J1: PMOD_02x06; PinHeader_2x06_P2.54mm_Vertical
J2: Conn_01x04; PinHeader_1x04_P2.54mm_Vertical
R1: 50; R_0603_1608Metric
R2, R3: 4.7k; R_0603_1608Metric
U1: W25N01GVZEIG; SON127P800X600X80-9N-D; Manufacturer_Part_Number W25N01GVZEIG; Mouser Part Number 454-W25N01GVZEIG
U2: RX8010SJ; SOIC127P600X265-8N; Manufacturer_Part_Number RX8010SJ

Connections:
/FLASH_CLK: J1.7, U1.6 (CLK)
/FLASH_CS: J1.10, U1.1 (~CS)
/FLASH_IO0: J1.9, U1.5 (DI(IO0))
/FLASH_IO1: J1.12, U1.2 (DO(IO1))
/FLASH_IO2: J1.11, U1.3 (~WP(IO2))
/FLASH_IO3: J1.5, U1.7 (~HOLD(IO3))
/I2C_SCL: J1.8, J2.2, R2.2, U2.6 (SCL)
/I2C_SDA: J1.6, J2.3, R3.2, U2.5 (SDA)
GND: C1.1, C2.2, C3.1, J1.3, J1.4, J2.4, U1.4 (GND), U1.9 (EP), U2.4 (GND)
unnamed: C2.1, D2.2, R1.2
unnamed: C3.2, D1.1, D2.1, R1.1, U2.8 (VDD)
VDD: C1.2, D1.2, J1.1, J1.2, J2.1, R2.1, R3.1, U1.8 (VCC)

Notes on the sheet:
PMOD-Flash TinyRTC


Board: 2 copper layers, 32.2 x 21.4 mm, 12 parts (0 on the bottom side), 12 nets.
